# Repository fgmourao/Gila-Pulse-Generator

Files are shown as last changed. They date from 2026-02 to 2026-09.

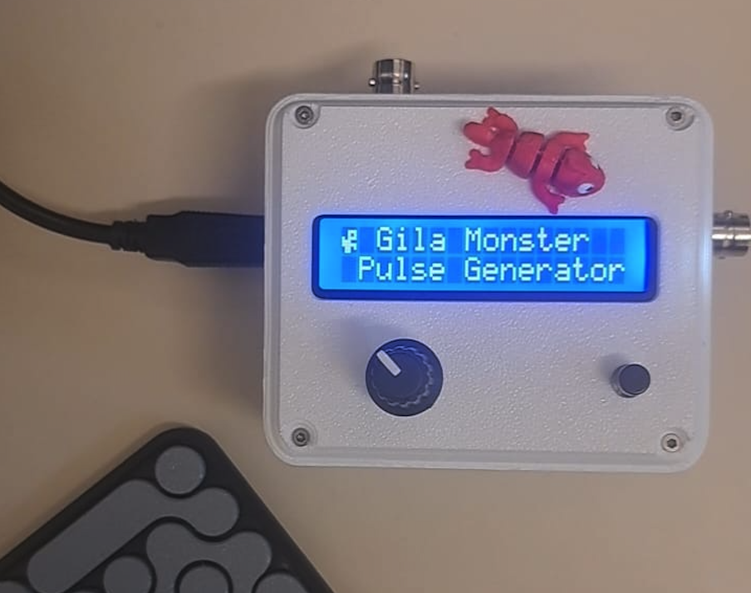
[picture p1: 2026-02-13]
Images/1.png

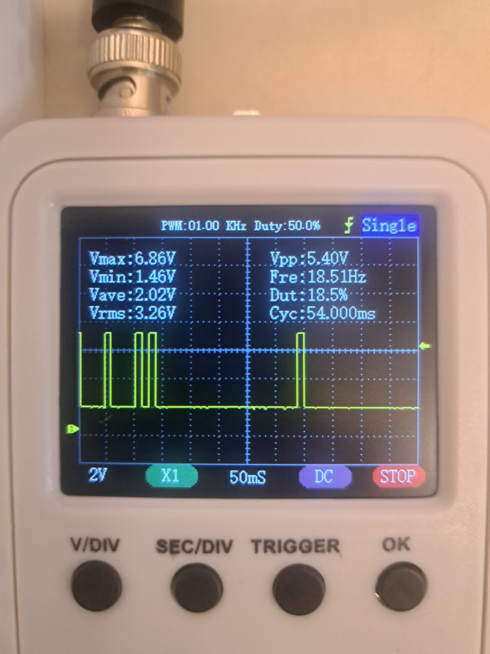
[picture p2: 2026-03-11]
Images/NPS_NPS_4pulses_20ms.jpeg

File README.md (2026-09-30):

# 🦎 Gila Monster 
### Pulse generator v1.0 

To meet the need for a pulse generator capable of triggering external instruments in neurostimulation protocols with multiple frequency patterns, the Gila Monster v1.0 was developed. Although numerous DIY solutions are available in online repositories, this project intentionally adopts a minimalist hardware design, centered on an Arduino Uno built around the ATmega328P microcontroller.

The design prioritizes the timing engine at both the hardware and firmware levels to ensure reliable, time-critical pulse generation.<br/>

## Firmware Specifications

- **Stimulation Modes:** Multi-engine pulse generation supporting Continuous (periodic), Burst (trains with inter-burst gaps), and Non-Periodic Stimulation (NPS) with randomized intra-window intervals (for NPS, see https://doi.org/10.1016/j.yebeh.2019.106609).

- **Time Base:** Microsecond-level timing relying on the 16 MHz system clock. Due to AVR hardware prescaling, the fundamental temporal resolution (software polling step) advances in 4 µs increments. Pulses are scheduled on a time grid, so timing errors do not accumulate from one pulse to the next.

- **Frequency Range & Resolution:** Programmable output frequency from 0.1 Hz to 500 Hz, with a 0.01 Hz resolution.

- **Pulse Width (PW) Range:** Fixed time from 0.10 ms (Continuous and Burst) or 0.05 ms (NPS) up to 999.99 ms, in 0.01 ms steps, or Duty Cycle in 0.01 % steps.

- **Output Control & Switching Latency:** Direct port manipulation using PORTD, bit 7 (PD7) to minimize software overhead, achieving a theoretical minimum switching latency of ≈125 ns (limited by the ATmega328P single instruction cycle).

- **Output Logic Level:** 5 V TTL-compatible digital output.

- **External Triggering & Synchronization:** Hardware interrupt on Pin D3 (INT1) with user-selectable Rising or Falling edge detection. In Trigger mode, the external trigger starts the whole programmed session, exactly as switching State ON does in Manual mode, and the session Timer is counted from the trigger. Triggers arriving while a session is running are ignored; when the session ends, the generator is armed again and the next trigger starts a new session. With Timer = 0 the session has no end and runs until stopped. The interrupt registers the event and the session starts in the main loop, with a measured trigger-to-output latency ~40 µs.

- **Single-Shot Diagnostic:** Manual pulse via Pin D6, debounced in firmware (100 ms of stable contact), delivering one pulse with the programmed width per press. Interlocked with the master state: operational only when State is OFF.

- **Duty Cycle Safety Clamp:** The output always returns LOW for at least 100 µs between pulses, which prevents 100 % duty cycle. The maximum pulse width is PWmax = T − 100 µs, applied to the displayed value.

- **Parameter Storage:** Non-volatile EEPROM storage of the 13 operational parameters, protected by a signature. Absent or invalid data loads the default settings.

- **Serial Communication:** UART interface (9600 baud) reporting the active configuration, the effective pulse timing in microseconds, a report of the last session and NPS simulation data for offline analysis.

## Build

Arduino IDE, board "Arduino Uno" (ATmega328P). Required libraries: ClickEncoder, TimerOne and LiquidCrystal_I2C.

## Serial Monitor

`Py_GilaMonster_Monitor.py` is a companion application that reads the Comm report over USB and displays it: session parameters, pulse count and timing faults on one side, the inter-stimulus interval distribution on the other, with export of the values (.txt) and of the plots (.png). It is passive and never writes to the port.

Opening a serial port resets the Arduino Uno (DTR auto-reset), so connect before switching the generator ON, or fit a 10 µF capacitor between RESET and GND to disable it.

Requires PyQt5, pyserial, numpy and matplotlib.

## Note on Usage and Constraints

Detailed usage instructions, as well as comprehensive operational constraints, hardware limitations and measured timing accuracy, are documented in the user manual.
Bench validation results (pulse counts, edge timing and session behaviour) are reported in the bench test document.

## License

- to be defined

## Future Development
v2.0 — Hardware Timer Architecture  

The current firmware relies on a polling-based timing engine inside loop(). Interference from the user interface is avoided by locking the interface during stimulation, and edge placement is protected by masking interrupts around each edge, but the resolution remains bound to the 4 µs step of the software time base.

The proposed architecture uses Timer1 (16-bit) in CTC mode with the output pin driven by the compare units (OC1A/OC1B): the interrupt only programs the next action, while the pin itself is switched by hardware with 62.5 ns resolution, independently of interrupt latency. The encoder service moves to Timer2. This would remove the 4 µs quantization and the interrupt masking altogether, and would allow the interface to remain live during stimulation. The output would move from D7 to D9.

The main challenges are periods longer than the 16-bit range of Timer1, which require chaining overflows in the interrupt, and the revalidation of the whole timing engine. NPS itself ports well, since the interval vector is already computed in the main loop and only consumed by the scheduler.

## Author

Flavio Mourao (mourao.fg@gmail.com)  
CNPq/MCTI/FNDCT Call No. 21/2024 — Grant No. 446467/2024-3
Federal University of Minas Gerais, Brazil

Development started: February 2024  
Last update: Sep 2026

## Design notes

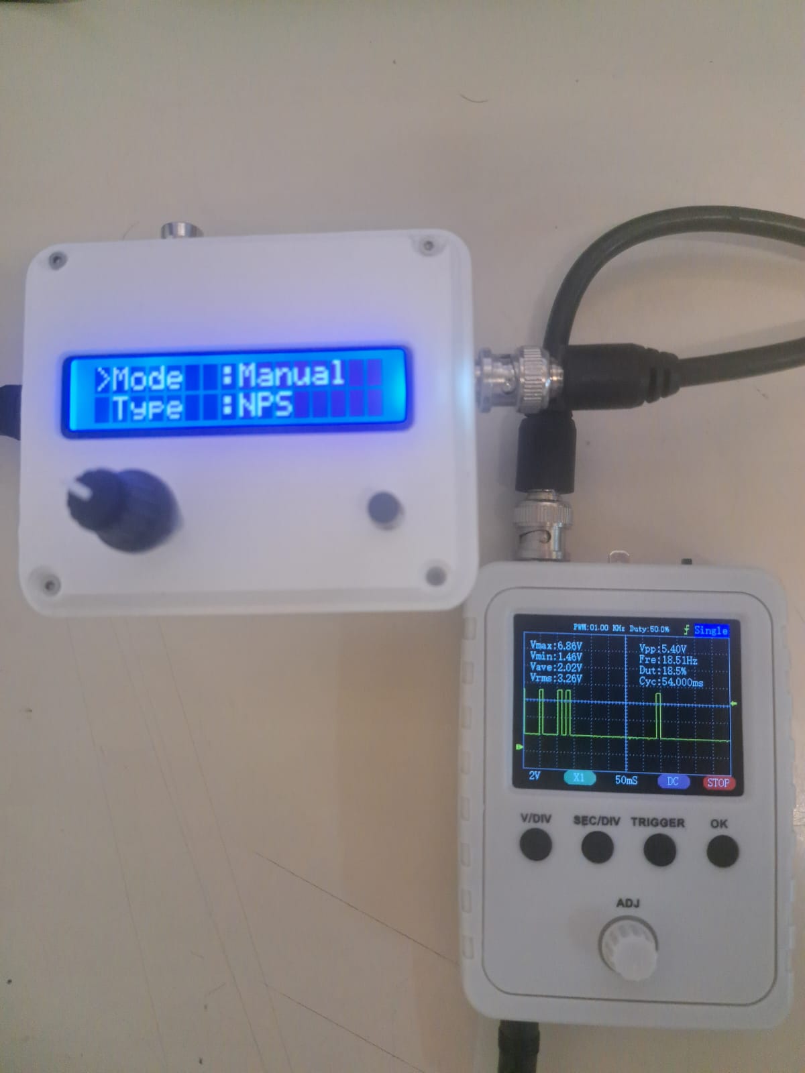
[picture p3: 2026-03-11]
Images/NPS_4pulses_20ms.jpeg

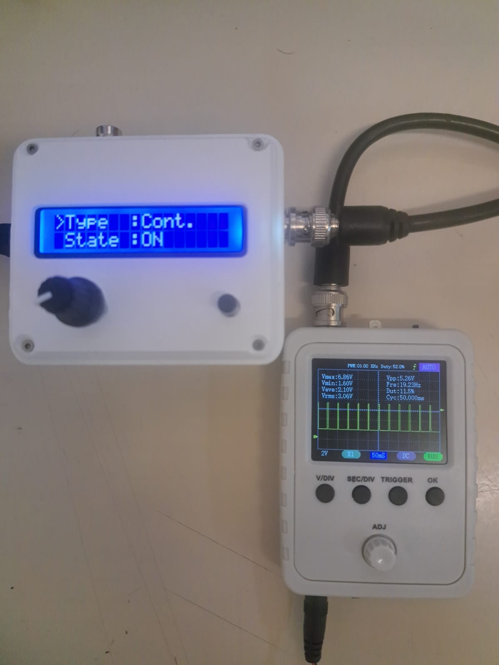
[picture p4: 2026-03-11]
Images/Continuous.jpeg

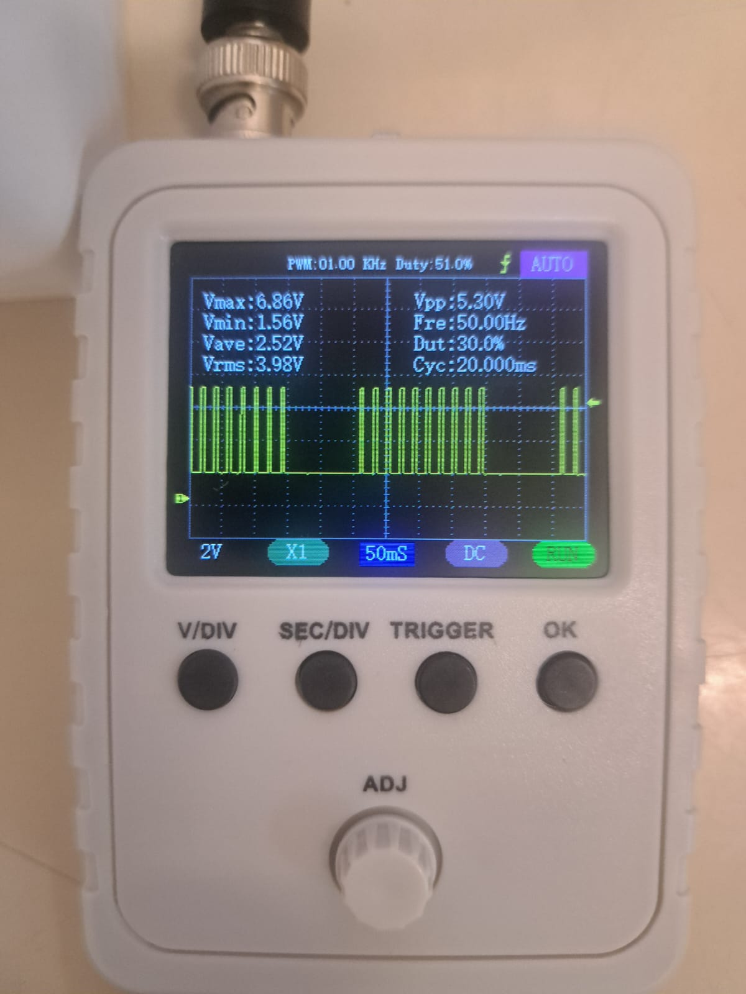
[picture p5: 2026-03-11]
Images/Burst_1.jpeg

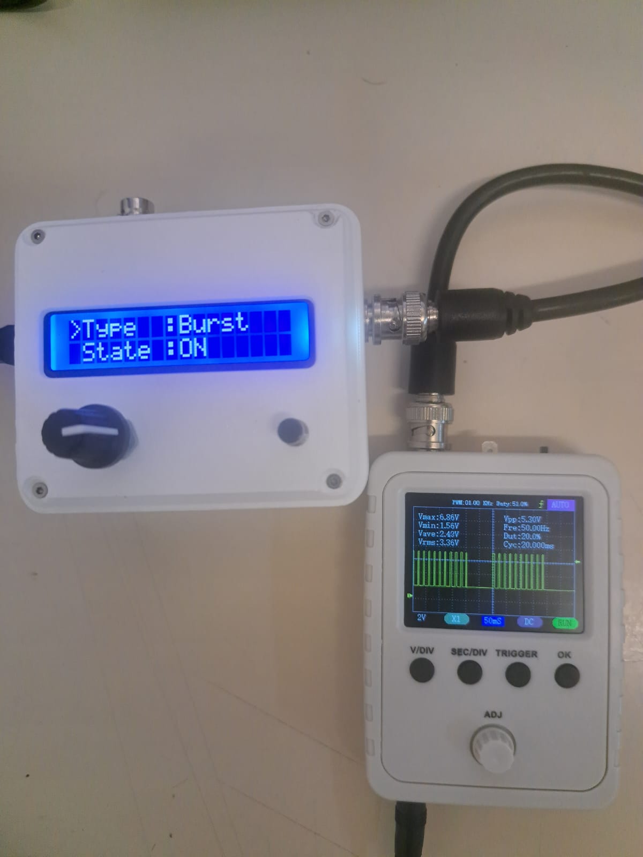
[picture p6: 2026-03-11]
Images/Burst.jpeg

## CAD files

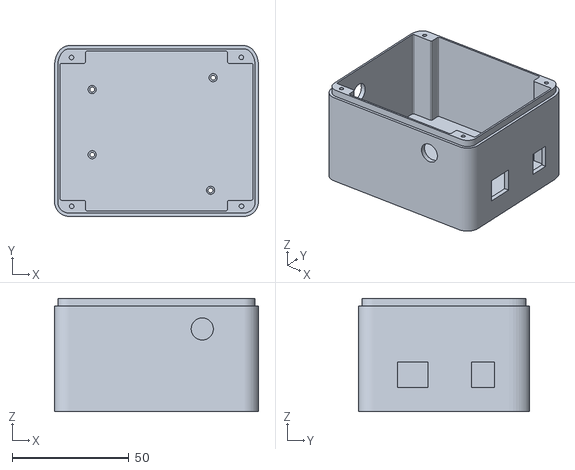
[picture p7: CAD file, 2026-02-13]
3D case/case_base_.stl
87.5 x 73.2 x 48.6

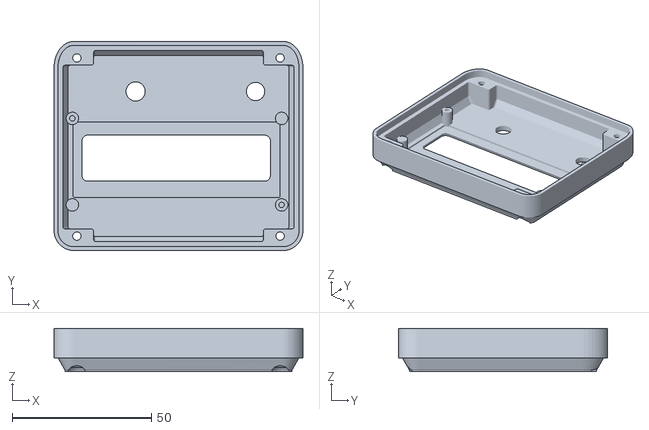
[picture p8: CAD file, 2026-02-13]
3D case/case_top_final_.stl
89.3 x 75.0 x 15.4

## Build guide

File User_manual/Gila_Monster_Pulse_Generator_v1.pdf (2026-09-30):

Gila Monster
Pulse generator v1.0

To meet the need for a pulse generator capable of triggering external instruments in neurostimulation

protocols with multiple frequency patterns, the Gila Monster v1.0 was developed. Although numerous DIY

solutions are available in online repositories, this project intentionally adopts a minimalist hardware design,

centered on an Arduino Uno built around the ATmega328P microcontroller. The design prioritizes the timing

engine at both the hardware and firmware levels to ensure reliable, time-critical pulse generation.

Project developed by:

Flavio Afonso Goncalves Mourao — mourao.fg@gmail.com

CNPq/MCTI/FNDCT Call No. 21/2024 — Grant No. 446467/2024-3

Federal University of Minas Gerais, Brazil

Documentation licensed under

Creative Commons Attribution-NonCommercial 4.0 International (CC BY-NC 4.0).

### 1. Firmware Specifications

- Stimulation Modes: Multi-engine pulse generation supporting Continuous (periodic), Burst (trains

with inter-burst gaps), and Non-Periodic Stimulation (NPS) with randomized intra-window intervals

(see, reference Cota et al.)

- Time Base: Microsecond-level timing relying on the 16 MHz system clock. Due to AVR hardware

prescaling, the time base (micros()) advances in 4 µs increments.

- Frequency Range & Resolution: Programmable output frequency from 0.10 Hz to 500.00 Hz,

with 0.01 Hz resolution.

- Pulse Width (PW) Range: Fixed time from 0.10 ms (Continuous and Burst) or 0.05 ms (NPS) up

to 999.99 ms, in 0.01 ms steps, or Duty Cycle in 0.01 % steps. Measured edge accuracy is ±4 µs

in all modes (Section 6.3).

- Output Control & Switching Latency: Direct port manipulation using PORTD, bit 7 (PD7), a single

2-cycle instruction (≈125 ns at 16 MHz).

- Output Logic Level: 5 V TTL-compatible digital output.
- External Triggering & Synchronization: Hardware interrupt on Pin D3 (INT1) with user-

selectable Rising or Falling edge detection. In Trigger mode, the external trigger then starts the

whole programmed session, exactly as switching State ON does in Manual mode, and the session

Timer is counted from the trigger. Triggers arriving while a session is running are ignored. The

interrupt registers the event and the session starts in the main loop, with a measured trigger-to-

output latency of ~30 to ~50 µs.

- Single-Shot Diagnostic: Manual pulse via Pin D6, debounced in firmware (100 ms of stable

contact), delivering one pulse with the programmed width per press. Interlocked with the master

state: operational only when State is OFF.

- Duty Cycle Safety Clamp: The output always returns LOW for at least 100 µs between pulses,

which prevents 100 % duty cycle (DC latching). The maximum pulse width is PWmax = T − 100 µs,

applied to the displayed value.

- Parameter Storage: Non-volatile EEPROM storage of the 13 operational parameters, protected

by a signature. Absent or invalid data loads the default settings.

- Serial Communication: UART interface (9600 baud) reporting the active configuration, the

effective pulse timing in microseconds, a report of the last session and NPS simulation data for

offline analysis.

### 2. Operating Engines

### 2.1 Deterministic Engine (Continuous [Periodic] / Burst Modes)

The deterministic timing engine computes the output period (T) as a direct function of the programmed

frequency (f), according to:

T (µs) = 1,000,000 / f (Hz)

Each rising edge is scheduled at the previous scheduled edge plus T, and each falling edge at the rising

edge plus PW. Because edges are referenced to this absolute grid, the long-term frequency is exact and

the per-pulse error does not accumulate.

In Continuous Mode, pulses are generated at a fixed period until the Timer expires or the user stops.

In Burst Mode, pulse delivery is governed by:

- a pulse counter defining the exact number of pulses per train (Count), delivered at period T;
- a silent-state timer (Gap), defined as the silence from the falling edge of the last pulse of a train to

the rising edge of the first pulse of the next train. The resulting cycle time is:

Cycle = (Count − 1) × T + PW + Gap

A Gap of 0 ms produces a single train, after which the generator switches itself OFF.

### 2.2 Non-Periodic Stimulation (NPS) Engine

The Non-Periodic Stimulation (NPS) engine implements a constrained uniform distribution algorithm to

generate temporally irregular pulse trains while preserving overall pulse density. Although the underlying

random selection is uniform within constrained temporal bounds, the sequential dependency between

events produces a heavy-tailed distribution of inter-stimulus intervals (ISI). As a result, shorter ISIs occur

more frequently while longer intervals remain possible, yielding a power-law-like temporal structure rather

than a purely Poisson or periodic pattern.

- Algorithm (1,000 ms window, t0 = 0):

tk = max(Random(tk−1, Endk) , tk−1 + ITImin)

Endk = 1000 − (N − k) × ITImin

where:

N | number of pulses in the window (Pulse Count)
k | index of the pulse being placed, from 1 to N
tk | timestamp of pulse k, in ms from the start of the window (t0 = 0)
ITImin | minimum interval between two pulses, in ms
Endk | latest time pulse k can occur while still leaving ITImin for each of the remaining N − k pulses

Random uniform draw in milliseconds

Each timestamp is drawn uniformly between the previous one and the remaining window space, and then

pushed forward if it falls closer than ITImin.

- Window Size: Fixed 1,000 ms temporal window. Timestamps are integer milliseconds.
- Pulse Density: Exactly N pulses per window (Pulse Density Modulation). With N × ITImin < 1000
| ms every timestamp falls inside the window, and every interval, including across consecutive
| windows, is at least ITImin.
- Temporal Structure: Inter-stimulus intervals (ISI) follow an inverse distribution of the form f(x) =
| k/x, that is, a power law with unitary exponent (β = 1). With the parameters of the original reference,
| N = 4 and ITImin = 20 ms, intervals range from 20 ms to 1860 ms. Other combinations of N and
| ITImin change the shape of the interval distribution and should be verified with the Comm export
| before use.

References by Cota, et al.

https://doi.org/10.1016/j.yebeh.2019.106609

https://doi.org/10.1016/j.yebeh.2008.09.006

### 3. Parameter Matrix & Data Mapping

ID Parameter | Type | Logic / Range | Resolution
00 Mode | Option | Manual (0) / Triggered (1) | N/A
01 Trigger Edge Option | Falling (0) / Rising (1) (Triggered mode only) | N/A
02 Type | Option | Continuous (0) / Burst (1) / NPS (2) | N/A
03 State | Action | OFF / ON | N/A
04 Frequency | Decimal 0.10 – 500.00 Hz (Cont. and Burst mode only) | 0.01 Hz
05 Pulse Count | Integer | 1 – 999 pulses (Burst mode) / 1 – 50 pulses and
| | N × ITImin < 1000 ms (NPS mode) | 1 pulse
06 Gap | Integer | 0 – 999,999 ms (Burst mode only; 0 = single train) | 1 ms
07 Minimum ITI | Integer | 1 – 999 ms (NPS mode only) | 1 ms
08 Width | Option | Fixed (0) / Duty Cycle (1) (NPS: Fixed only) | N/A
09 Pulse | Decimal Fixed: 0.10 – 999.99 ms (NPS: from 0.05 ms), limited
| | to T − 0.1 ms (NPS: ITImin − 0.1 ms).
| | Duty Cycle: equivalent limits in % | 0.01 ms / 0.01
| | | %
10 Timer | Integer | 0 (Disabled) – 999,999 ms | 1 ms
11 Save | Action | “SAVED” | N/A
12 Comm | Action | “SENT” | N/A

Several limits depend on other parameters (Frequency, Minimum ITI and Pulse Count). When a change

makes another value invalid, that value is corrected and the LCD shows Auto-adjusted followed by the

name of the parameter that changed. Parameters that do not apply to the selected mode are hidden from

the menu.

### 4. Hardware Interface (Pinout)

Digital & Analog Pin Assignment

MCU

Pin

Arduino

Pin | Direction Pull-Up | Function | Notes
PD7 | D7 | Output | Disabled Pulse Output | High-speed TTL output. i.e. use 220 Ω

series resistor for opto-isolation or long

cables.

PD3 | D3 | Input | Enabled | Hardware

Trigger (INT1)

External interrupt input, Rising or Falling

edge. The pull-up keeps the line HIGH

when unconnected.

PD2 | D2 | Input | Enabled | Encoder

Channel A

(CLK)

Quadrature decoding. Internal pull-up

reduces noise and wiring complexity.

PD5 | D5 | Input | Enabled | Encoder
| | | | Channel B
| | | | (DT)
Quadrature | decoding. | Matched | with

Channel A.

PD4 | D4 | Input | Enabled | Encoder Push
| | | | Button (SW) | Active-low user input. Debounced in
| | | | | firmware.
PD6 | D6 | Input | Enabled | Single Shot
| | | | Button | Manual pulse fire. Debounced (100 ms)
| | | | | and interlocked with master state (State
| | | | | OFF only).
PC4 | A4 | I/O | Enabled | I²C SDA | Shared data line. Standard-mode 100 kHz.
| | | | | External pull-ups optional if LCD provides
| | | | | them.
PC5 | A5 | Output | Enabled | I²C SCL | Shared clock line. Standard-mode 100
| | | | | kHz.

### 5. Serial Communication & Data Validation

The COMM [12] function operates as a diagnostic and validation interface, providing access to internal

configuration and timing behavior via the serial port.

- Protocol: UART serial communication at 9600 baud, 8-N-1.
- Configuration: mode, output type and the parameters of the active type, including the effective

period and the effective HIGH time of the pulse in microseconds.

- Last Session Report: number of pulses fired and number of timing faults (edges placed more than

50 µs late). A correct session reports 0 timing faults.

- Monte Carlo Validation (NPS Mode): the firmware simulates an NPS session with the current

parameters and exports the resulting inter-stimulus intervals as a single CSV column [ITI_ms], for

offline analysis of ISI variability and power-law fitting. The simulated duration is the programmed

Timer, or 10 s when the Timer is disabled.

Notes for open-hardware users:

- COMM and SAVE are only available when State is OFF. Simulation and data export never run

concurrently with stimulation.

### 6. Operational Constraints and Architectural Limitations

### 6.1 Firmware Logic & Safety Constraints

- Parameter Limits: Limits are applied to the parameter values. When a change forces another

parameter to change, the LCD shows Auto-adjusted and the name of that parameter.

- Pulse Width Limits: Minimum HIGH time of 100 µs in Continuous and Burst modes and 50 µs in

NPS mode. Minimum LOW time of 100 µs between pulses, so PWmax = T − 100 µs

(Continuous/Burst) or ITImin − 100 µs (NPS), applied to the displayed value. The firmware cannot

produce a constant-high output: every pulse is followed by at least 100 µs at logic low, which

prevents continuous current injection into the preparation.

- NPS Window Constraint: The pulses of a window must fit inside it: N × ITImin < 1000 ms. The

menu enforces this by limiting the Pulse Count to the largest value that satisfies it, so increasing

the Minimum ITI may reduce the Pulse Count, which is signaled by Auto-adjusted.

- NPS Pulse Width: In NPS mode the pulse width is always a fixed time, since there is no period to

refer a duty cycle to.

- NPS Pulse Count Hard Limit: The maximum number of pulses per window is 50. Timestamps are

held in two statically allocated buffers of 50 entries (the window being played and the next window

being prepared) in the ATmega328P’s 2 KB SRAM. Increasing this value would risk memory

exhaustion and undefined behavior.

- Locked Interface: While State is ON, the knob is ignored, the LCD is not redrawn and Save/Comm

are unavailable. The only accepted input is a click on State, which stops the generator.

- Clean Stop: Stopping, by click or by the Timer, always lets the current pulse finish. A pulse is never

truncated or prolonged by the stop command. A stop during a Burst ends the train after the current

pulse.

- Session Timer: The session starts when State is switched ON in Manual mode, or at the trigger

in Trigger mode. Only pulses whose rising edge is scheduled before the end of the session are

emitted. At 1 Hz with Timer = 10,000 ms, exactly 10 pulses are delivered (at 0, 1, …, 9 s). In Burst

mode, the last train may be cut by the end of the session.

- Trigger Operation: In Trigger mode, switching State ON arms the generator without producing

any output. The external trigger then starts the whole programmed session, a continuous train, a

sequence of bursts or a sequence of NPS windows, exactly as switching State ON does in Manual

mode. Triggers arriving while a session is running are ignored, so a session always runs as

programmed. When the session ends, the generator is armed again and the next trigger starts a

new one. With Timer = 0 a session has no end and runs until stopped, so only one trigger is

accepted.

- Single-Shot Diagnostic Logic: The Single-Shot button (D6) is only operational when State is

OFF. A press is accepted after 100 ms of stable contact and delivers one pulse with the

programmed width, regardless of how long the button is held. Presses shorter than 100 ms are

ignored, which limits manual firing to about 5 presses per second.

### 6.2 Timing Architecture & Hardware-Induced Limitations

- Polling Engine with Scheduled Edges: The main loop compares micros() with the next scheduled

edge. When an edge is less than 400 µs away, the CPU busy-waits for it with interrupts masked

and then writes the port. No interrupt can run between the time check and the port write.

- Masked Interval: Interrupts are masked for at most about 0.8 ms per edge, less than the 1.024 ms

Timer0 overflow, so the system clock never loses counts. Encoder and trigger interrupts that occur

during this interval are deferred.

- Resolution Limit: The time base advances in 4 µs steps, which bounds the placement error of

each edge to about ±4 µs. Sub-microsecond resolution would require dedicated hardware timers

(e.g. CTC mode), which this architecture does not use.

- Clock Tolerance: The ATmega328P on the Arduino Uno R3 is clocked by a ceramic resonator,

typically accurate to about ±0.5 %. All timings scale with it (e.g. a programmed 500 Hz may

measure between about 497.5 and 502.5 Hz). Relative timing within a protocol is unaffected.

Measuring the actual frequency of each unit once with an oscilloscope or frequency counter is

recommended.

- Trigger Latency: The trigger interrupt only registers the event; the session starts when the main

loop processes it. The resulting latency (~30 to ~50 µs) varies from trigger to trigger. When sub-

100 µs synchronization matters, record the D7 output together with the external signal and use D7

as the timing reference.

- Timing Fault Monitor: Any edge placed more than 50 µs late is counted and reported by Comm,

providing a per-session integrity check.

### 6.3 Temporal Accuracy

Pulse width and period test:

Configuration | Pulses Programmed PW | Measured PW | Programmed T | Measured T
Cont. 1 Hz | 60 | 100 µs | 97.0 – 103.3 µs | 1,000,000 µs | ±3.6 µs
Cont. 20 Hz | 400 | 5 ms | 4,997.0 – 5,004.0 µs | 50,000 µs | ±3.6 µs
Cont. 500 Hz | 9,999 | 100 µs | 97.0 – 103.8 µs | 2,000 µs | ±3.8 µs
Burst 50 Hz × 10 | 100 | 2 ms | 1,996.9 – 2,003.4 µs | 20,000 µs | ±3.4 µs
NPS 4/s | 120 | 100 µs | 97.1 – 103.5 µs | – | –
NPS 50/s | 999 | 50 µs | 49.2 – 54.7 µs | – | –

100 % of the measured pulse widths and periods fell within ±4 µs of the programmed value (99.7 % for the

50 µs NPS pulses). The mean frequency at 500 Hz was 499.9999 Hz.

Protocol structure and counting:

Test | Expected | Measured
Burst: pulses per train (50 Hz, Count 10) | 10 | 10 in 10/10 trains
Burst: Gap (Gap = 1,818 ms) | 1,818,000 µs 1,817,997.8 – 1,818,000.3 µs
Burst: cycle time | 2,000,000 µs 1,999,997.8 – 2,000,002.3 µs
NPS: pulses per window (N = 4, ITImin 20 ms) | 4 | 4 in 28/28 windows
NPS: pulses per window (N = 50, ITImin 19 ms) | 50 | 50 in 18/18 windows
NPS: shortest interval (ITImin 20 ms / 19 ms) | ≥ ITImin | 19.998 ms / 18.996 ms
Timer: 1 Hz, Timer = 10,000 ms | 10 pulses | 10 pulses
Trigger: session start (1 Hz, Timer = 10,000 ms) 10 pulses | 10 in every complete session
Trigger: triggers arriving during a session | ignored | 6 of 12 ignored
Trigger: trigger-to-output latency (114 triggers) | – | 28.9 – 51.3 µs (mean 37.8, p99 46.7)

The NPS shortest intervals are below ITImin by at most 4 µs, the resolution of the time base.

### 7. Operation Modes

### 7.1 Continuous Mode (Periodic)

Generates a constant flow of pulses at a fixed frequency. This is the simplest operational mode, suitable

for protocols requiring regular, periodic stimulation without temporal structure.

Example Configuration: 20 Hz stimulation with 5 ms pulse width.

Parameter Value

Type | Cont.
Freq | 020.00 Hz
Width | Fixed
Pulse | 005.00 ms
State | ON

Measured: pulse width 4,997.0 – 5,004.0 µs; period 50,000 ± 3.6 µs (duty cycle 10 %).

### 7.2 Burst Mode

Generates groups of pulses (trains) separated by a configurable silence interval (Gap). Suitable for

protocols requiring episodic stimulation with controlled inter-train intervals.

Example Configuration: 10 pulses at 50 Hz with 2 ms pulse width, repeating every 2 seconds.

Parameter Value

Type | Burst
Freq | 050.00 Hz
Count | 010
Gap | 001818 ms
Width | Fixed
Pulse | 002.00 ms
State | ON

Note: Cycle = (Count − 1) × T + PW + Gap. At 50 Hz, 10 pulses span 9 × 20 ms + 2 ms = 182 ms. For a

2,000 ms cycle, Gap = 2,000 − 182 = 1,818 ms.

Measured: 10 pulses in every train; cycle 2,000,000 ± 2.3 µs; pulse width 1,996.9 – 2,003.4 µs.

### 7.3 NPS Mode (Non-Periodic Stimulation)

Generates a specific number of pulses per 1,000 ms window at randomized intervals. Suitable for protocols

requiring temporal unpredictability while preserving overall pulse density.

Example Configuration: 4 random pulses per second with 100 µs pulse width, at least 20 ms between

pulses.

Parameter Value

Type | NPS
Count | 004
ITImin | 020 ms
Width | Fixed
Pulse | 000.10 ms
State | ON

NPS Constraint Validation:

N × ITImin = 4 × 20 ms = 80 ms < 1,000 ms

Pulse count within hard limit: 4 ≤ 50

Pulse width within limit: 0.10 ms ≤ ITImin − 0.1 ms = 19.9 ms

Measured: 4 pulses in every window; shortest interval 19.998 ms; pulse width 97.1 – 103.5 µs.

Recommended: before an experiment, use Comm to export the simulated ISI sequence for the chosen

Count and Minimum ITI and check the interval distribution offline.

### 8. Assembly Instructions

### 8.1 Electronics

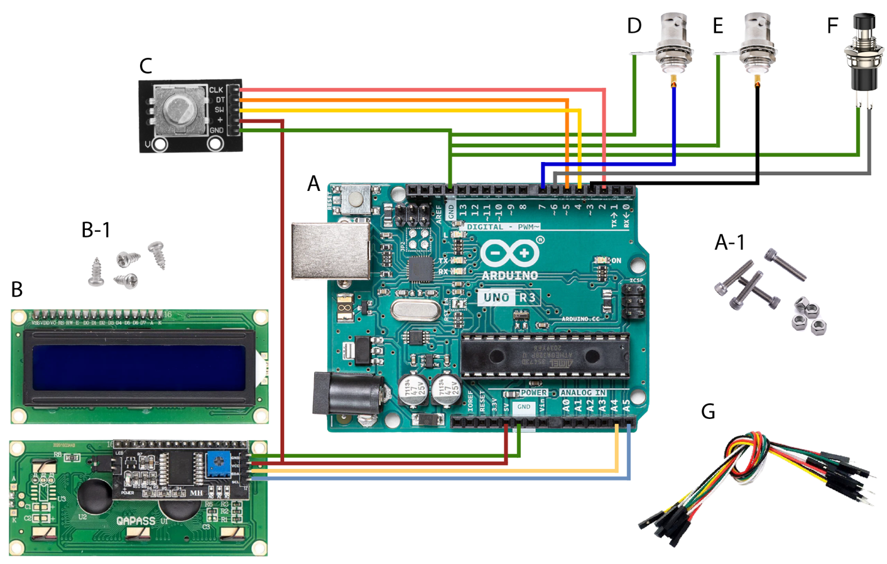
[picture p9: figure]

| Materials | Quantity | Link | $
A | Arduino Uno R3 | 1 | Mouser electronics | 25.87
A-1 | M2 x 12 mm Allen Bolt Socket Cap Screws
| M2 Hex Nut for Arduino | 4 | - | -
B | LCD module 16x2, (WxHxD): 80x36x13 mm
| I2C LCD display module | 1 | Amazon | 10
B-1 | Round Head Tap Screw for LCD Ø 2-2.5 mm,
| L = 3-6 mm) | 4 | - | -
C | 360 Rotatory encoder module KY-040 | 1 | Amazon | ~7 (2 un)
D, E | Female BNC panel-mount | 2 | - | -
F | Push Button RS PBS 110 | 1 | Amazon | ~.60
G | Cables, different colors (e.g. Ø 2.5 mm,
| cross section 0,5 mm², length 10-15 cm) | ~15 | Amazon | ~5 (40 un)

8.2 3D parts

- PLA case (WxHxD): 7.5 x 6 x 8.5 cm
- 4 M2 x 20 mm Allen Bolt Socket Cap Screws

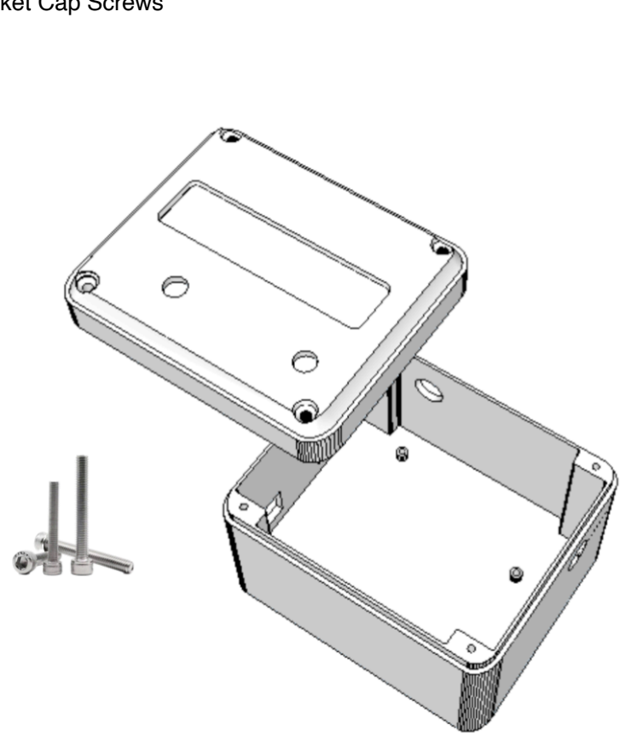
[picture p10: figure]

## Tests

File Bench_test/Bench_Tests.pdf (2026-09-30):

Gila Monster — Pulse generator v1.0

Bench Test Report

Unit under test: Gila Monster v1.0, single output port (D7), Arduino Uno R3 (ATmega328P, 16 MHz).

Instruments: digital oscilloscope, 1 MΩ DC-coupled probe on D7; firmware session report over the serial

port (Comm, 9600 baud, 8-N-1).

Session length: 300 s (Timer = 300,000 ms) unless stated otherwise.

Reported quantities: Pulses fired and Timing faults are taken from the firmware session report. A timing

fault is an edge placed more than 50 µs after its scheduled time.

### 1. Edge timing

Quantity | Specification | Measured
Pulse width | programmed value ±4 µs | within ±4 µs
Period | programmed value ±4 µs | within ±4 µs
Dominant jitter location | – | falling edge

Edge placement resolution is bound by the 4 µs step of the micros() time base. Rising edges are scheduled

on an absolute time grid; falling edges are referenced to the rising edge and therefore do not always

coincide with the grid.

### 2. Continuous mode

# | Configuration | Expected | Measured Faults

1 | 500.00 Hz, Fixed 0.10 ms (T = 2,000 µs, PW = 100 µs) | 150,000 pulses | 150,000 | 0
2 | 0.10 Hz, Fixed 100.00 ms (T = 10 s, PW = 100 ms) | 30 pulses | 30 | 0
3 | 20.00 Hz, Fixed 5.00 ms (duty 10 %) | 6,000 pulses | 6,000 | 0
5 | 100.00 Hz, Duty Cycle 50.00 % | PW = 5,000 µs | 5,000 µs,
| | | 30,000 pulse | 0
17 20.00 Hz, Fixed 1.00 ms, Timer 600,000 ms | 12,000 pulses | 12,000 | 0

### 3. Parameter limits

# Configuration | Expected | Measured

4 500.00 Hz, Fixed 5.00 ms requested | clamped to 1.90 ms (T − 100 µs),
| Auto-adjusted | clamped to 1.90 ms, Auto-
| | adjusted shown
6 100.00 Hz, Duty Cycle 0.01 % requested | clamped to 1.00 % (100 µs floor) | clamped to 1.00 %, HIGH
| | time 100 µs

In both cases the limit is applied to the displayed value, and the output matches the display.

### 4. Burst mode

# Configuration | Expected Measured Faults

7 50.00 Hz, Count 10, Gap 1,818 ms, PW 2.00 ms | 1,500 pulses (150 trains) | 1,500 | 0
8 50.00 Hz, Count 1, Gap 0 ms | 1 pulse, generator
| switches OFF | 1 | 0
9 100.00 Hz, Count 999, Gap 5,000 ms, PW 2.00 ms | 20,016 pulses | 20,016 | 0

Test 7: cycle = (10 − 1) × 20 ms + 2 ms + 1,818 ms = 2,000 ms; 150 complete cycles in 300 s. The train

that would start exactly at the end of the session is not emitted.

Test 9: cycle = (999 − 1) × 10 ms + 2 ms + 5,000 ms = 14,982 ms; 20 complete cycles (19,980 pulses) plus

36 pulses of the train cut by the end of the session.

### 5. NPS mode

# | Configuration | Expected | Measured Faults

10 Count 4, ITImin 20 ms, PW 0.10 ms | 1,200 pulses,
| | no interval < 20 ms | 1,200,
| | | constraint met
| | | 0
11 Count 50, ITImin 19 ms, PW 0.05 ms | 15,000 pulses | 15,000 | 0
12 Count 1, ITImin 999 ms, PW 0.05 ms 300 pulses, intervals of 1,000 ms | 300, all ITI
| | 1,000 ms | 0

Test 11 is the upper bound of the mode: 50 × 19 ms occupies 95 % of the window, so most draws fall below

the minimum interval and are pushed to it, and the train degenerates towards a periodic one.

### 6. Session Timer

# | Configuration | Expected Measured Faults

13 | Cont. 1.00 Hz, Timer 10,000 ms | 10 pulses (at 0, 1, … 9 s) | 10 | 0
14 | Burst 2.00 Hz, Count 10, Gap 1,000 ms, PW
| 100.00 ms, Timer 3,300 ms | 7 pulses, last pulse not
| | truncated | 7, full
| | | width | 0
14b Cont. 1.00 Hz, PW 500.00 ms, Timer 2,500 ms | 3 pulses, third one
| complete

3, full

width

0

Only pulses whose rising edge is scheduled before the end of the session are emitted. A pulse already in

progress is always completed.

### 7. Trigger mode and manual firing

# | Configuration | Expected | Measured

15 Trigger, Cont. 1.00 Hz,

| Timer 10,000 ms | trigger starts the session; triggers during the session
| | ignored; next trigger starts a new session | as
| | | expected
16 State | OFF, | Single-Shot
| button (D6) | one pulse per press, programmed width, no repeat
| | while held | as
| | | expected

### 8. Summary

All 17 tests met their expected result. Pulse counts matched the computed values exactly in every mode,

including the cases where the session Timer cuts a burst. No timing faults were reported in any session,

including sessions of 150,000 pulses. Measured pulse width and period were within ±4 µs of the

programmed values, consistent with the resolution of the time base.

Not covered by this report: absolute clock accuracy (the Arduino Uno R3 ceramic resonator is typically

within ±0.5 %, and all timings scale with it), which requires an external time reference; and the statistical

verification of the NPS interval distribution, which is done offline from the Comm export.

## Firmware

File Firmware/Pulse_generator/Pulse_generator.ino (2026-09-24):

/* * 
 * PROJECT: Gila Monster Pulse Generator
 * VERSION: 1.0
 * AUTHOR:  Flavio Afonso Goncalves Mourao — mourao.fg@gmail.com
            CNPq/MCTI/FNDCT Call No. 21/2024 — Grant No. 446467/2024-3
            Federal University of Minas Gerais, Brazil

 * DEVELOPMENT STARTED: February, 2024           
 * LAST UPDATE: September, 2026

 * DESCRIPTION:
 * Pulse generator designed for Arduino Uno (ATmega328P) across three operational modes:
 * Continuous, Burst, and Non-Periodic Stimulation (NPS).

 * MODES OF OPERATION:
 * 1. Continuous : Regular, periodic pulse trains at a specific frequency.
 * 2. Burst      : Clustered groups of pulses separated by a customizable inter-burst gap.
 * 3. NPS        : "Non-Periodic Stimulation". Pulses are placed within each 1-second window by a
 *                 sequential shrinking-window algorithm, yielding power-law distributed
 *                 inter-pulse intervals, obeying a minimum interval.
 *                  Ref: https://doi.org/10.1016/j.yebeh.2019.106609
 *                  Ref: https://doi.org/10.1016/j.yebeh.2008.09.006 
 *
 * KEY FEATURES & SAFETY:
 * - Time Base       : Microsecond resolution (4 us steps). Pulse edges are placed by busy-waiting
 *                     on micros() when an edge is near.
 * - LCD = Output    : Limits are applied to the menu values, so the LCD always shows what the pin
 *                     produces. If a change forces another parameter to change, the LCD shows
 *                     "Auto-adjusted" and the name of that parameter.
 * - Safety Clamps   : Minimum HIGH time 100 us (Cont/Burst) or 50 us (NPS). Minimum LOW time
 *                     100 us between pulses (no 100% Duty Cycle / latched output).
 * - Locked UI       : While generating, the knob, LCD redraws, Save and Comm are disabled.
 *                     Only a click on State (stop) is accepted.
 * - Clean Stop      : Stopping (click or Timer) always lets the current pulse finish.
 * - Single-Shot     : Debounced manual button, fires one pulse with the programmed width.
 * - Non-Volatile    : EEPROM storage of all experimental parameters (with signature).
 * - Diagnostics     : Comm reports pulses fired and timing faults of the last session.
 *
 * PROTOCOL SEMANTICS:
 * - Continuous (Manual) : a pulse every 1/Freq until Timer or stop.
 * - Burst (Manual)      : Count pulses at 1/Freq. Gap is the silence from the falling edge of the
 *                         last pulse to the rising edge of the next burst. Gap = 0: single burst.
 * - NPS (Manual)        : Count pulses in every 1-second window, windows back-to-back.
 * - Trigger mode        : The external trigger then starts the whole programmed session, exactly as 
 *                         switching State ON does in Manual mode, and the session Timer is counted from the trigger.
 *                         Further triggers are ignored until the session ends; after that the
 *                         generator is armed again and the next trigger starts a new session.
 *                         With Timer = 0 a session has no end, so it runs until stopped.
 * - Timer               : only pulses whose rising edge is before the end of the session are
 *                         emitted (1 Hz with Timer = 10000 ms gives 10 pulses).
 * - NPS constraints     : Width is Fixed, Count x ITImin < 1000 ms, Pulse <= ITImin - 0.1 ms.
 *
 * HARDWARE I/O & SYNCHRONIZATION :
 * - OUTPUT (Pin D7) : Main 5V TTL stimulation pulse to drive the output stage.
 * - INPUT  (Pin D3) : External Trigger IN. Interrupt-driven, to start protocols synchronously
 *                     with external behavior software.
 * - MANUAL (Pin D6) : Single-Shot manual firing button input (only when State = OFF).
 *
 * MENU REFERENCE (LCD Interface):
 * [0] Mode   : Manual (Auto-run) or Trigger (Waits for external D3 signal).
 * [1] Edge   : Signal type for External Trigger (Rising or Falling edge).
 * [2] Type   : The Generation Engine (Cont, Burst, or NPS).
 * [3] State  : The Master Switch (ON / OFF).
 * [4] Freq   : Frequency (0.10 to 500.00 Hz). Used in Cont./Burst modes.
 * [5] Count  : Pulse amount (Pulses per Burst, or Pulses per Second in NPS).
 * [6] Gap    : Inter-burst silence (ms). Used in BURST mode.
 * [7] ITImin : Minimum time between random pulses (integer ms). Used in NPS mode.
 * [8] Width  : Logic for pulse duration (Fixed time [ms] vs Duty Cycle [%]).
 * [9] Pulse  : The High-time duration.
 * [10] Timer : Session length from switching ON (0 = disabled).
 * [11] Save  : Saves current settings to EEPROM.
 * [12] Comm  : Serial dump of parameters, last session report and NPS simulation data to PC.
 */
// =================================================================================
// LIBRARIES

#include <ClickEncoder.h>       // Rotary Knob
#include <TimerOne.h>           // Internal clock handling
#include <EEPROM.h>             // Save settings when power is off
#include <Wire.h>               // LCD communication
#include <LiquidCrystal_I2C.h>  // Display

// =================================================================================
// 1. HARDWARE CONNECTIONS

#define TRIGGER_PIN 3          // Input for External Trigger

#define ENCODER_PIN_A 2        // Knob Pin A. Rotary Encoder CLK
#define ENCODER_PIN_B 5        // Knob Pin B. Rotary Encoder DT
#define ENCODER_PIN_BUTTON 4   // Rotary Encoder Switch (SW)

#define SINGLE_PULSE_PIN 6     // The manual "Fire" button for single pulse

#define OUTPUT_PIN 7           // The output pin

// Initialize the Screen and the Knob
LiquidCrystal_I2C lcd(0x27, 16, 2);
//LiquidCrystal_I2C lcd(0x3F, 16, 2);

ClickEncoder encoder(ENCODER_PIN_B, ENCODER_PIN_A, ENCODER_PIN_BUTTON, 4);

// =================================================================================
// 2. CONSTANTS

#define MIN_HIGH_US_STD   100UL   // Minimum pulse width, Cont/Burst
#define MIN_HIGH_US_NPS    50UL   // Minimum pulse width, NPS
#define MIN_LOW_US        100UL   // Minimum LOW time between two pulses
#define SPIN_WINDOW_US    200UL   // If an edge is closer than this, busy-wait for it
#define LATE_TOLERANCE_US  50UL   // An edge later than this is counted as a timing fault
#define NPS_STEP_GUARD_US 1000UL  // Only compute NPS timestamps when no edge is this close
#define NPS_WINDOW_US  1000000UL  // NPS window: 1 second

#define EEPROM_MAGIC   0x414C4947L  // "GILA"
#define EEPROM_VERSION 1L
#define EEPROM_DATA    8            // Menu values start after magic + version

// =================================================================================
// 3. GLOBAL VARIABLES

// Helpers for the Menu System
int edit_digit = 0;                     // Which digit are we editing? (1s, 10s, 100s...)
uint32_t digit_multipliers[] = {100000, 10000, 1000, 100, 10, 1};
byte dinoChar[8] = { B00000, B00111, B00101, B10111, B11100, B11111, B01101, B01100 }; // The little lizard logo

// State Flags (shared with the trigger interrupt)
volatile bool generating = false;       // Master Switch: true = ON, false = OFF
volatile bool triggerEvent = false;     // Did we receive an external signal?
volatile bool isTriggerMode = false;    // External pin?
int last_edge_mode = -1;                // Remembers if we trigger on Rising or Falling edge
bool armed_for_start = false;           // Engine is armed in loop(), after the LCD has been redrawn

// --- PULSE ENGINE STATE (only touched from loop) ---
bool pulse_active = false;              // Output is HIGH right now
uint32_t pulse_start_us = 0;            // Rising edge time of the active pulse
bool train_active = false;              // A next rising edge is scheduled
uint32_t next_pulse_us = 0;             // Scheduled time of the next rising edge
long pulsesRemaining = 0;               // Pulses left in the current burst
bool counted = false;                   // Current train has a finite number of pulses
bool stop_requested = false;            // End the session as soon as the current pulse ends
bool session_active = false;            // A programmed session is running
bool power_off = false;                 // The stop also switches the generator OFF
bool have_last_end = false;             // last_pulse_end_us is valid
bool pending_finish = false;            // A pulse ended; on_pulse_finished() still has to run
uint32_t last_pulse_end_us = 0;         // Falling edge time of the last pulse

// Session report (shown by Comm)
uint32_t session_pulses = 0;            // Pulses fired in the last session
uint16_t timing_faults = 0;             // Edges placed later than LATE_TOLERANCE_US

// --- NPS SPECIFIC VARIABLES (For the Random Mode) ---
#define MAX_NPS_PULSES 50               // Maximum pulses per second allowed in NPS

// One NPS vector, generated one timestamp at a time.
typedef struct {
  uint16_t t[MAX_NPS_PULSES];           // Timestamps (ms) inside the 1 s window
  uint8_t n;                            // Number of pulses in the window
  uint8_t i;                            // How many timestamps are already generated
  uint16_t d;                           // Minimum interval (ms)
  long ini;                             // Algorithm state
  long fim;                             // Algorithm state
  bool ready;                           // All n timestamps generated
} NpsGen;

NpsGen nps_bufs[2];
NpsGen* nps_active = &nps_bufs[0];      // Vector being played
NpsGen* nps_pending = &nps_bufs[1];     // Vector being prepared for the next window
uint8_t nps_idx = 0;                    // Next pulse in the active vector
uint32_t nps_window_start_us = 0;       // Start of the current window
bool nps_window_open = false;           // A window has been started (trigger mode)

// Timing Variables
bool in_menu = false;                   // Are we currently editing a number?
bool val_change = true;                 // Do we need to redraw the screen?
uint32_t period_us = 0;                 // Calculated period in microseconds
uint32_t pulse_on_us = 0;               // Calculated pulse width in microseconds
uint32_t session_start_us = 0;          // Session start (same clock as the pulses, for Timer)
int adjusted_idx = -1;                  // Menu item changed automatically by a limit
// Manual button debounce: the button state only changes after the pin has been stable
// for BTN_STABLE_MS. One press = one pulse, however long it is held.
#define BTN_STABLE_MS 100
bool btnRaw = HIGH;                     // Last raw reading
bool btnStable = HIGH;                  // Debounced state
unsigned long btnChangeTime = 0;        // When the raw reading last changed

// =================================================================================
// 4. MENU STRUCTURE

enum menu_type { VALUE, ACTION, OPTION };

typedef struct {
  const char* name_;      // The text shown on LCD
  menu_type type;         // The type (VALUE/ACTION/OPTION)
  long value;             // The current setting
  long lim_min;           // Lowest allowed number
  long lim_max;           // Highest allowed number
  const char* options[3]; // List of text options
  const char* suffix;     // Unit label (Hz, ms, %)
} menu_item;

#define NUM_ITEMS 13 // Total number of menu pages
menu_item menu[NUM_ITEMS];
int menu_idx = 0;    // Which page are we looking at?

// =================================================================================
// 5. FUNCTION PROTOTYPES
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
